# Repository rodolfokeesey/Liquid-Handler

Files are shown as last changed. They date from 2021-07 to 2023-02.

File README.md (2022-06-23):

# Liquid-Handler

Welcome to the github page for the SideKick liquid handler!

The Sidekick is a desktop liquid dispensing robot, compatible with standard SBS microplates designed for accessible laboratory automation. The Sidekick features an armature-based motion system and a fully 3D printed chassis to reduce overall mechanical complexity and build time, and accommodate user modification. Liquid dispensing is achieved by using four calibration-free solenoid driven positive displacement  pumps that deliver 10 microliter increments. Control is provided over a USB serial interface using a simple vocabulary of commands, implemented in the form of a short Micro Python program. At a total price of $710, the Sidekick offers laboratories an easy to build, easily maintained, open-source liquid handling system for both research and pedagogical introductions to lab automation. 

A complete description of the project and build instructions is available in R. Keesey, R, LeSeur, J. Schrier, “Sidekick: A Low-Cost Open-Source 3D Printed Liquid Dispensing Robot” _Hardware X_ 12, E00319 (2022) [doi:10.1016/j.ohx.2022.e00319](https://doi.org/doi:10.1016/j.ohx.2022.e00319)  

You can also see a video of it in action online: https://www.youtube.com/watch?v=fTURNI88WFQ

But if you don't want to read the paper, and just want to get started with building, take a look at the assembly guide located in the "Supporting Documentation" folder. This currently covers the mechanical assembly, the wiring, and getting started with the Sidekick's software.

Copyright Rodolfo Keesey 2022.                                                    
                                                                             
This source describes Open Hardware and is licensed under the CERN-OHL-S v2. 
                                                                             
You may redistribute and modify this source and make products using it under 
the terms of the CERN-OHL-S v2 (https://ohwr.org/cern_ohl_s_v2.txt).         
                                                                             
This source is distributed WITHOUT ANY EXPRESS OR IMPLIED WARRANTY,          
INCLUDING OF MERCHANTABILITY, SATISFACTORY QUALITY AND FITNESS FOR A         
PARTICULAR PURPOSE. Please see the CERN-OHL-S v2 for applicable conditions.  
                                                                             
Source location: https://github.com/rodolfokeesey/Liquid-Handler                                        
                                                                             
As per CERN-OHL-S v2 section 4, should You produce hardware based on this    
source, You must where practicable maintain the Source Location visible      
on the external case of the Gizmo or other products you make using this      
source.

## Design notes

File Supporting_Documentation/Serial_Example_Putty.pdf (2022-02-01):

Step 1: Determining the COM port

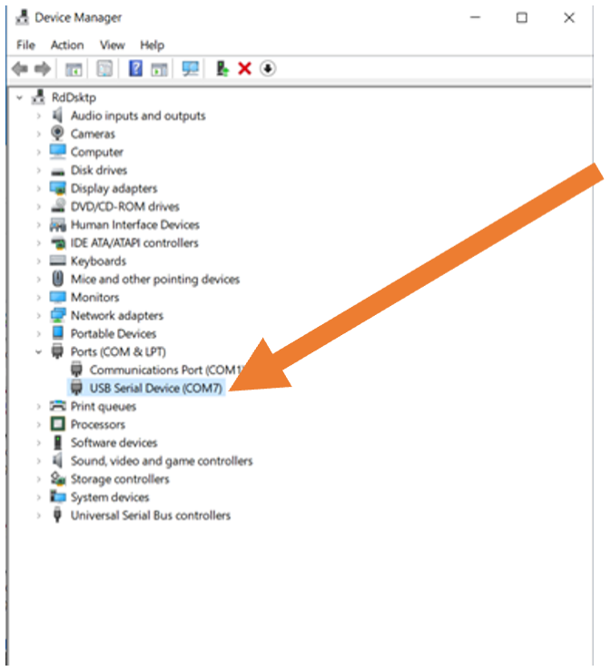
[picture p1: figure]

Figure 1: Checking the Sidekick COM port in Windows 10 device manager

The Sidekick reads commands from the USB serial port, allowing any application or programming environment that supports serial I/O to communicate with it. We recommend using Thonny or a serial terminal program such as Putty (on Windows), or the built-in “screen” command line program (on Mac/Linux).

To use Putty, first find the Sidekick’s com port, and baud rate. These are easy to find in Windows with the device manager. Go to Device Manager -> Ports -> USB Serial Device (Fig. 1). Our Sidekick is located at COM7 (on Windows) or /dev/tty.usbmodem0000000000001 (on Mac/Linux). If you are unsure which port your Sidekick occupies, unplug it, and see which port disappears.

Step 2: Determining Baud

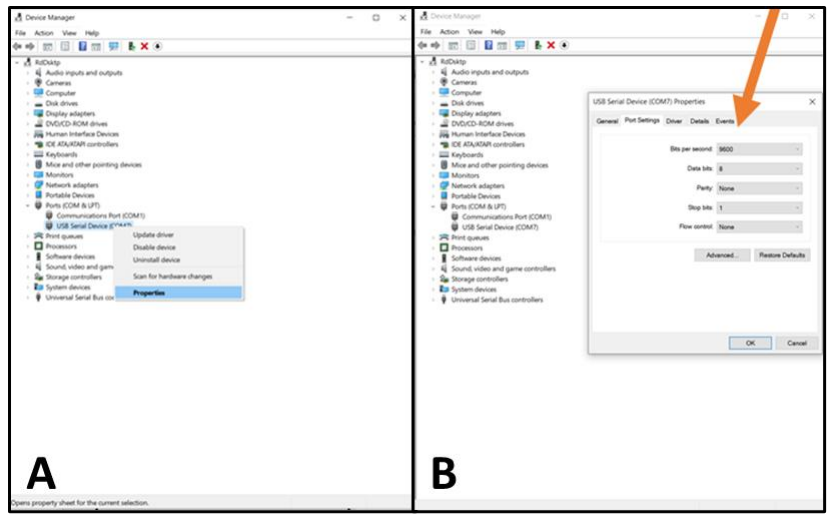
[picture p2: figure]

Figure 2A: Device Manager drop down. | B: Sidekick Baud in Device Manager Properties

Right click on the USB Serial Device. Click “Properties” in the drop down (Fig. 2a). Then click port settings. Make a note of the indicated bits per second, or baud (Fig. 2b).

Step 3: Connecting Via Putty

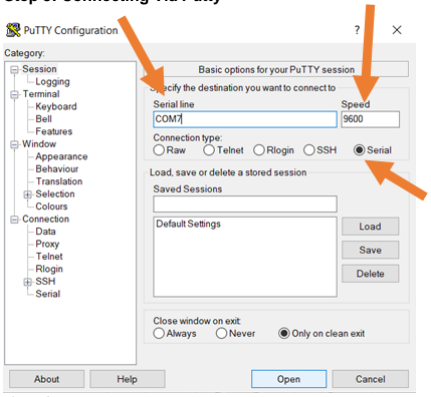
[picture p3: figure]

Figure 3: Putty startup UI

Now that we have the com port and the baud, we can use Putty to open a serial connection.
Download and install Putty: https://www.putty.org/
Once Putty is installed, open the application. Press the “Serial” option, and then input the correct com port we found in Step 1 under “Serial line”. Then input the baud rate we found in Step 3 under “Speed” (Fig. 3).
Step 4: Opening Putty and Sending Commands

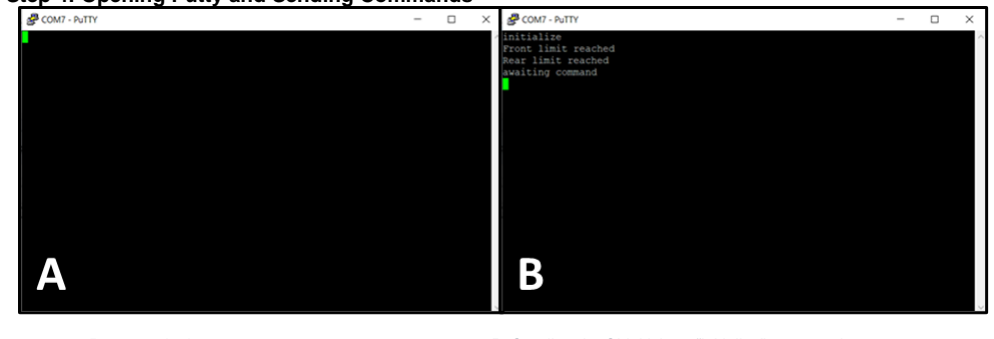
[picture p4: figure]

Figure 4a: Putty terminal | B: Sending the Sidekick an “initialize” command

After pressing open, the command line screen will appear (Fig. 4a). Type “initialize” (followed by return) to test communication with the Sidekick (Fig. 4b). The Sidekick should home against the limit switches, and output to the terminal. The Sidekick is now online and prepared to receive commands.

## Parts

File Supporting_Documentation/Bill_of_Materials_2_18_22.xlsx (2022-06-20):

Item | Items needed | Items per Unit Purchased | Units Purchased | Unit Cost | Bulk Cost (100 units) | Total Cost | Cost per Item needed | Link | Alternate Link | Comments
Overture PETG 1KG | 1 | 1 | 1 | 22.99 | NA | 22.99 | 22.99 | https://www.amazon.com/OVERTURE-Filament-Consumables-Dimensional-Accuracy/dp/B07PGYHYV8?s=industrial
3x10x4mm Ball bearings | 3 | 10 | 1 | 9.99 | NA | 9.99 | 2.997 | https://www.amazon.com/uxcell-Groove-Bearing-Double-Bearings/dp/B07FW257LJ
M2/3/4 Hardware (Button Head) | 1 | 1 | 1 | 23.99 | NA | 23.99 | 23.99 | https://www.amazon.com/Stainless-Assortment-820PCS-VIGRUE-Washers/dp/B098KXZNY6?s=industrial
M3 Hardware | 1 | 1 | 1 | 11.99 | NA | 11.99 | 11.99 | https://www.amazon.com/Stainless-Assortment-Precise-Beautiful-Printed/dp/B0714FLXND
PTFE Tubing 1/16" OD | 1 | 5 | 1 | 40.31 | NA | 40.31 | 8.062 | https://www.amazon.com/Cole-Parmer-PTFE-Tubing-32-Pack/dp/B00PQZUD3I
PTFE Tubing 1/8" OD | 1 | 5 | 1 | 59.35 | NA | 59.35 | 11.87 | https://www.amazon.com/Cole-Parmer-PTFE-Tubing-16-pack/dp/B00T97OZD8
12 Volt PSU | 1 | 1 | 1 | 12.99 | NA | 12.99 | 12.99 | https://www.amazon.com/LEDMO-Power-Supply-Transformers-Adapter/dp/B01461MOGQ
Power Barrel | 1 | 1 | 1 | 1.25 | NA | 1.25 | 1.25 | https://www.sparkfun.com/products/119
Breakaway Male Header Pins (40 Count) | 5 | 1 | 5 | 1.5 | 0.23 | 7.5 | 7.5 | https://www.sparkfun.com/products/116
Buttons | 1 | 1 | 4 | 0.25 | 0.2 | 1 | 0.25 | https://www.digikey.com/en/products/detail/apem-inc/MJTP1230E/1795785
Jumper Cables | 22 | 120 | 1 | 7.98 | NA | 7.98 | 1.463 | https://www.amazon.com/gp/product/B07GCY6CH7/ref=ppx_yo_dt_b_asin_title_o04_s00?ie=UTF8&th=1
Limit Switch | 2 | 2 | 1 | 2.95 | NA | 2.95 | 2.95 | https://www.sparkfun.com/products/13014
The Lee Company Fixed Volume 10μL Dispense Pumps (LPMA1250110L) | 4 | 1 | 4 | 135 | 120 | 540 | 540 | https://www.theleeco.com/products/electro-fluidic-systems/dispense-pumps/fixed-volume-dispense-pumps/lpm-series-pumps/
PCB | 1 | 5 | 1 | 3.1 | NA | 3.1 | 0.62 | https://jlcpcb.com/
Micrcontroller (Raspberry Pi Pico) | 1 | 1 | 1 | 4 | NA | 4 | 4 | https://www.digikey.com/en/products/detail/raspberry-pi-(trading)-ltd/SC0915/13684020
Darlington Array | 1 | 10 | 1 | 7.99 | NA | 7.99 | 0.799 | https://www.amazon.com/Bridgold-ULN2803APG-ULN2803-Darlington-High-Voltage/dp/B07W5WRG56
Stepper Motor Driver | 2 | 5 | 1 | 28.99 | NA | 28.99 | 11.596 | https://www.amazon.com/FYSETC-Stepstick-Heatsink-Ramps1-4-Board-5Pcs/dp/B08M9J8SB7
0.9deg Nema 17 Stepper Motor Bipolar | 2 | 1 | 2 | 22.99 | NA | 45.98 | 45.98 | https://www.amazon.com/Stepper-Pancake-LDO-42STH25-1404MAC-Printer-Extruder/dp/B089G8HZ51 | https://www.aliexpress.com/item/2251832831935819.html?pdp_ext_f=%7B%22sku_id%22%3A%2267236436630%22%7D | The amazon provider often seems to be out of stock.
Prices and Links Valid as of 2/18/22 |  |  |  |  | Quantity 1, 4 Pump Configuration Cost: | 832.35
 |  |  |  |  | 4 Pump Configuration, Unit Cost | 711.297

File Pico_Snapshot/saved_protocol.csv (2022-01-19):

Pump | Location | Amount
p1 | a1 | 150
p1 | a2 | 150
p1 | a3 | 150
p1 | a4 | 150
p1 | a5 | 150
p2 | a6 | 150
p2 | a7 | 150
p2 | a8 | 150
p2 | a9 | 150
p2 | a10 | 150
p2 | a11 | 150
p2 | a12 | 150
p1 | b1 | 150
p1 | b2 | 150
p1 | b3 | 150
p1 | b4 | 150
p1 | b5 | 150
p3 | b6 | 150
p3 | b7 | 150
p3 | b8 | 150
p3 | b9 | 150
p3 | b10 | 150
p3 | b11 | 150
p3 | b12 | 150
p1 | c1 | 150
p1 | c2 | 150
p1 | c3 | 150
p1 | c4 | 150
p1 | c5 | 150
p2 | c6 | 150
p2 | c7 | 150
p2 | c8 | 150
p2 | c9 | 150
p2 | c10 | 150
p2 | c11 | 150
p2 | c12 | 150
p1 | d1 | 150
p1 | d2 | 150
p1 | d3 | 150
p1 | d4 | 150
p1 | d5 | 150
p3 | d6 | 150
p3 | d7 | 150
p3 | d8 | 150
p3 | d9 | 150
p3 | d10 | 150
p3 | d11 | 150
p3 | d12 | 150
p2 | e1 | 150
p2 | e2 | 150
p2 | e3 | 150
p2 | e4 | 150
p2 | e5 | 150
p2 | e6 | 150
p2 | e7 | 150
p2 | e8 | 150
p2 | e9 | 150
p2 | e10 | 150
p2 | e11 | 150
p2 | e12 | 150
p3 | f1 | 150
p3 | f2 | 150
p3 | f3 | 150
p3 | f4 | 150
p3 | f5 | 150
p3 | f6 | 150
p3 | f7 | 150
p3 | f8 | 150
p3 | f9 | 150
p3 | f10 | 150
p3 | f11 | 150
p3 | f12 | 150
p2 | g1 | 150
p2 | g2 | 150
p2 | g3 | 150
p2 | g4 | 150
p2 | g5 | 150
p2 | g6 | 150
p2 | g7 | 150
p2 | g8 | 150
p2 | g9 | 150
p2 | g10 | 150
p2 | g11 | 150
p2 | g12 | 150
p3 | h1 | 150
p3 | h2 | 150
p3 | h3 | 150
p3 | h4 | 150
p3 | h5 | 150
p3 | h6 | 150
p3 | h7 | 150
p3 | h8 | 150
p3 | h9 | 150
p3 | h10 | 150
p3 | h11 | 150
p3 | h12 | 150

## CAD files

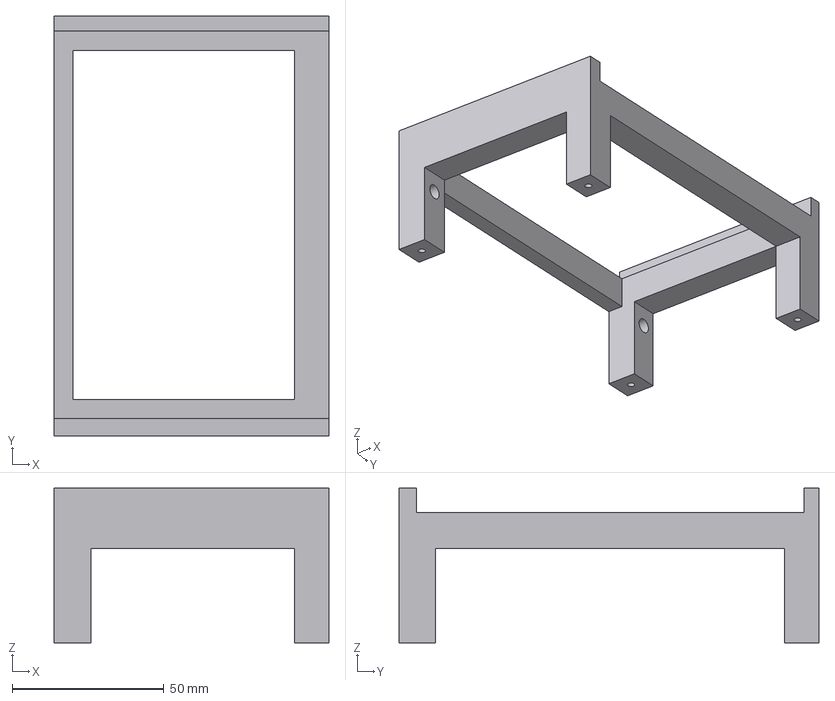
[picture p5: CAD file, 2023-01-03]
3D_Assets/96WellTrayHolder_Reservoir/96 Well Holder.step
90.6 x 138.5 x 51.1 mm

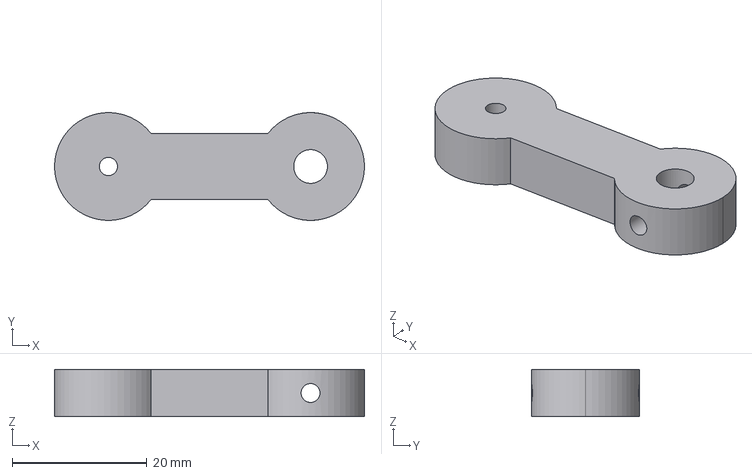
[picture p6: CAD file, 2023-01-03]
3D_Assets/Armature/Arm Two.step
46.0 x 16.0 x 7.00 mm

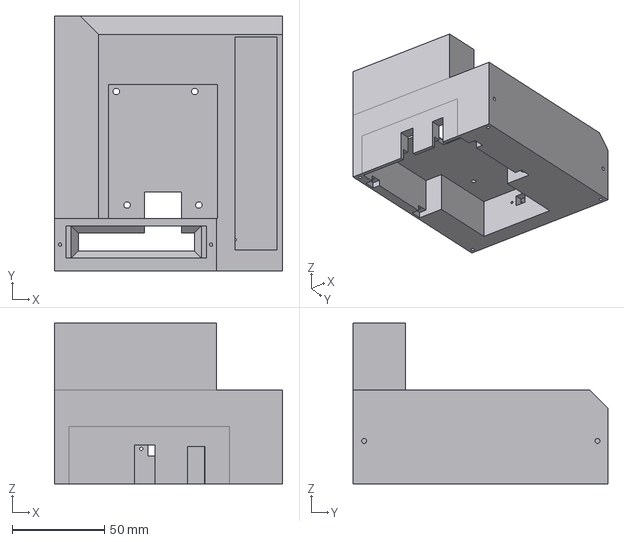
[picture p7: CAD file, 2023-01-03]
3D_Assets/MainBody/Base.step
124.0 x 138.5 x 87.2 mm

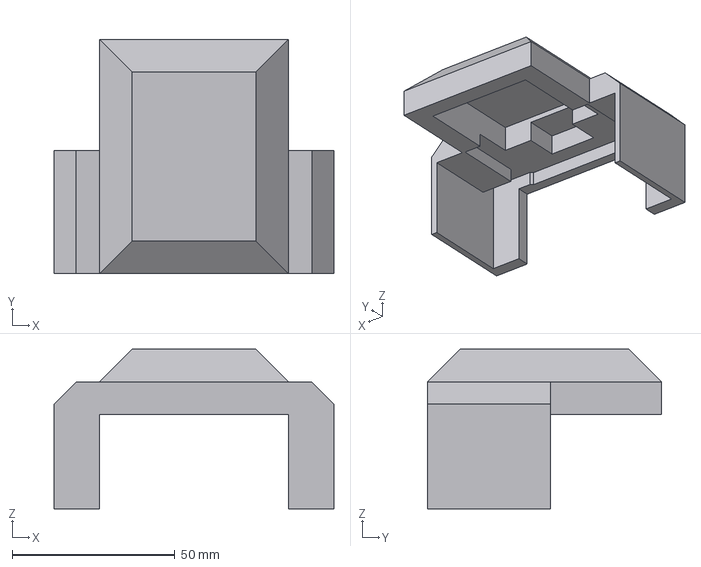
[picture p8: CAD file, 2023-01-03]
3D_Assets/MotorMounts/Motor Cap New (Unvalidated).step
86.0 x 72.0 x 49.0 mm

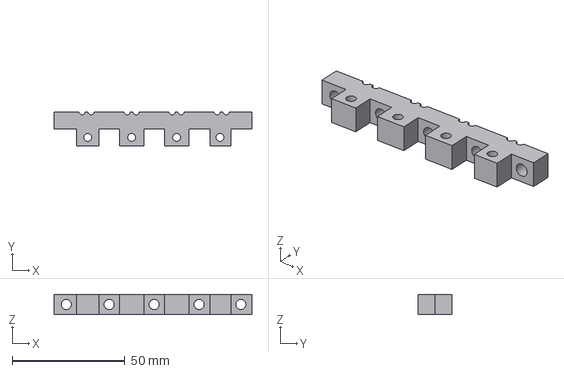
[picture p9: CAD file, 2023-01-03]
3D_Assets/Pumps/Front Adapter Clamp.step
88.0 x 15.3 x 9.00 mm

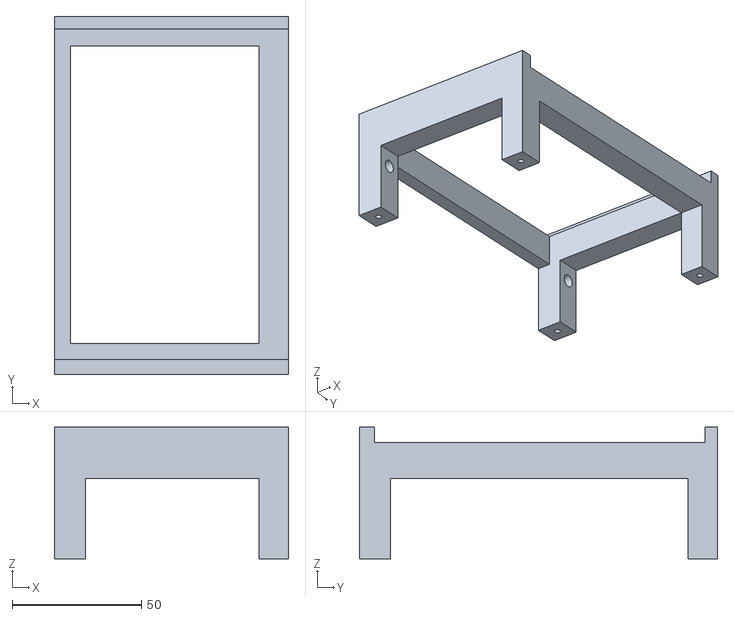
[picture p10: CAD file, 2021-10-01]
3D_Assets/96WellTrayHolder_Reservoir/96 Well Plate Holder.stl
90.5 x 138.5 x 51.0

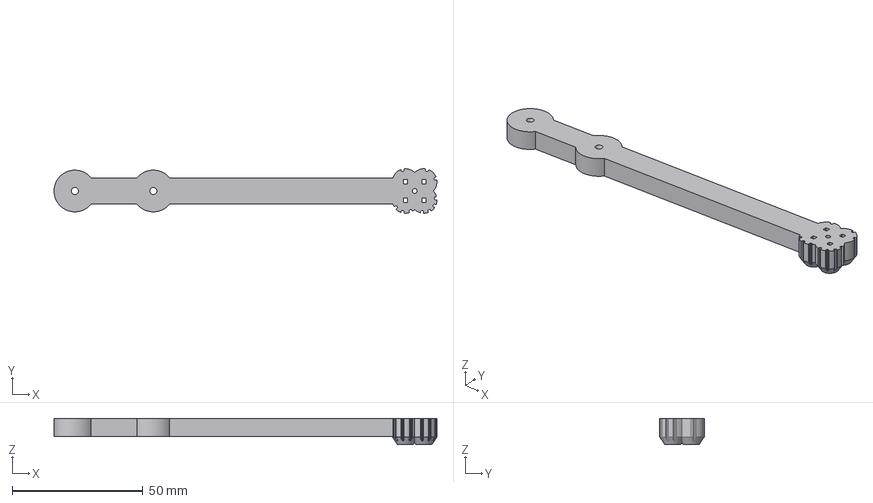
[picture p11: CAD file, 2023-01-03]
3D_Assets/Armature/Arm Four.step
146.5 x 17.1 x 10.0 mm

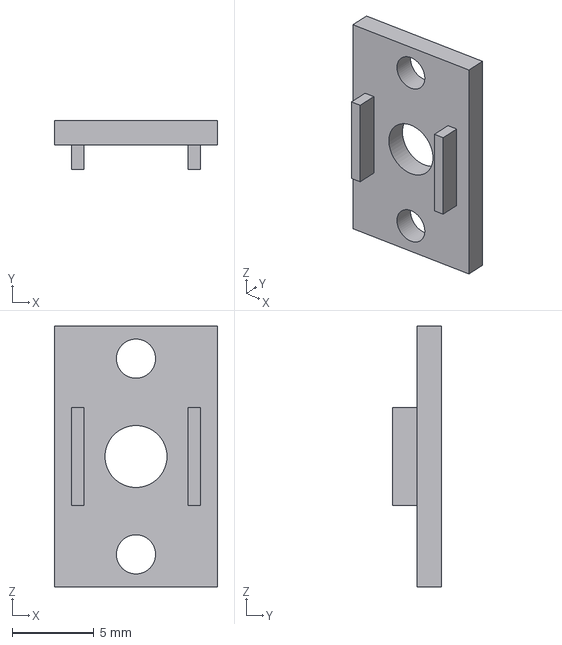
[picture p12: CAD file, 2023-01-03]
3D_Assets/MainBody/Button Housing Front.step
10.0 x 3.00 x 16.0 mm

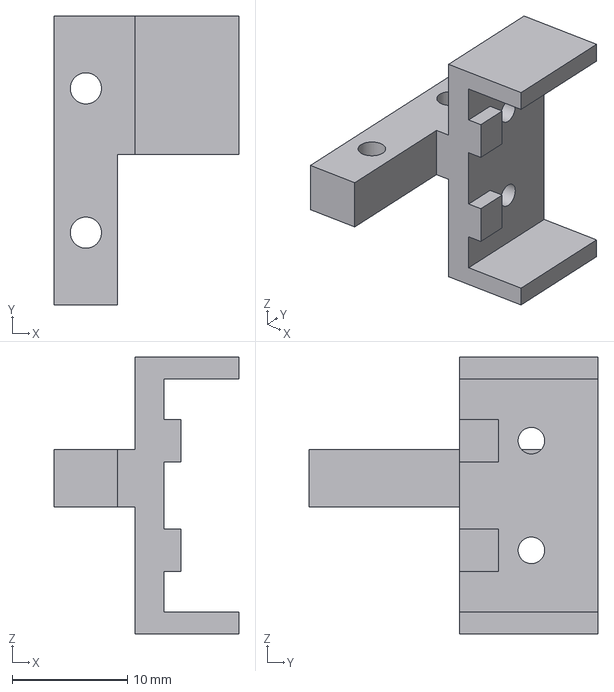
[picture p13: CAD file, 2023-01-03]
3D_Assets/MotorMounts/Front Switch Mount.step
16.0 x 25.0 x 24.0 mm

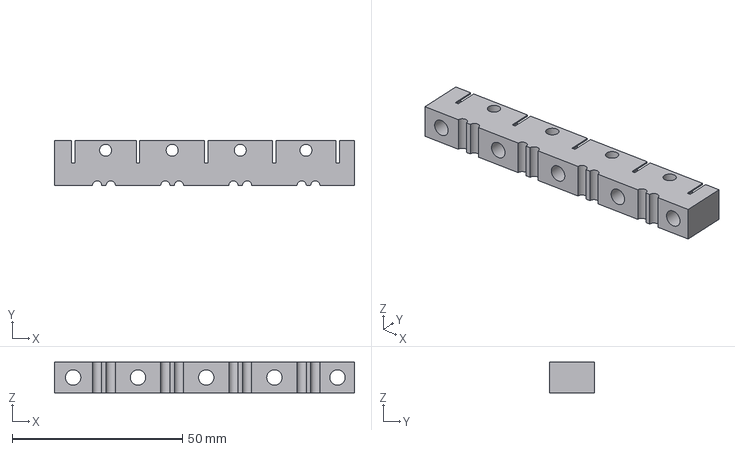
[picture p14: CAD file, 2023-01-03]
3D_Assets/Pumps/Rear Adapter Clamp.step
88.0 x 13.2 x 9.00 mm

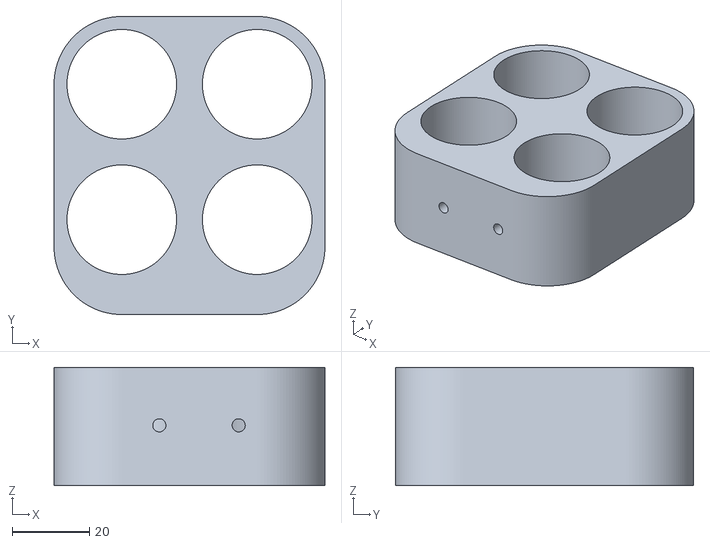
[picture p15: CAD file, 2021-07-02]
3D_Assets/96WellTrayHolder_Reservoir/50ml Tube Holder.stl
70.0 x 77.0 x 30.5

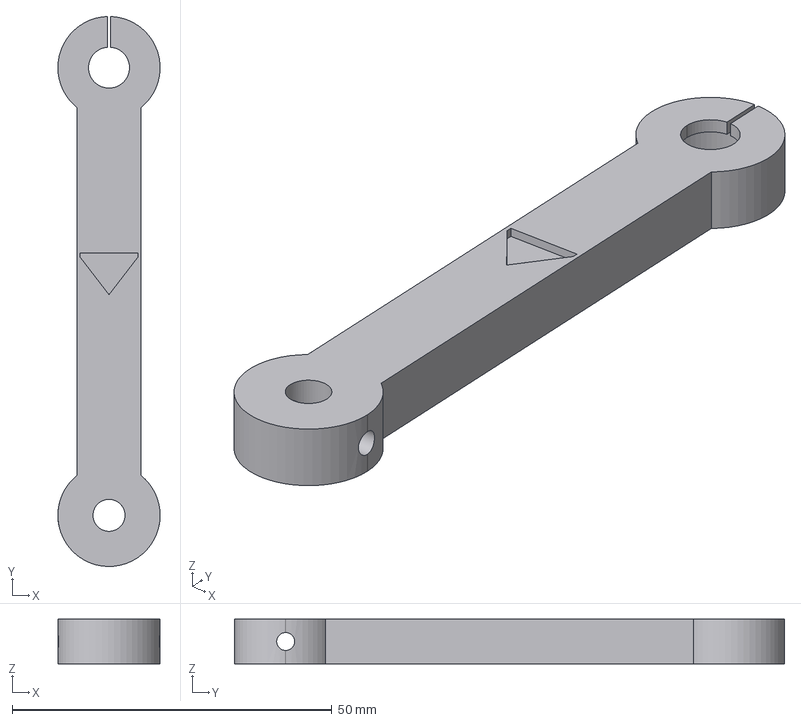
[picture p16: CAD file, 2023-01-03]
3D_Assets/Armature/Arm One.step
16.0 x 86.0 x 7.00 mm

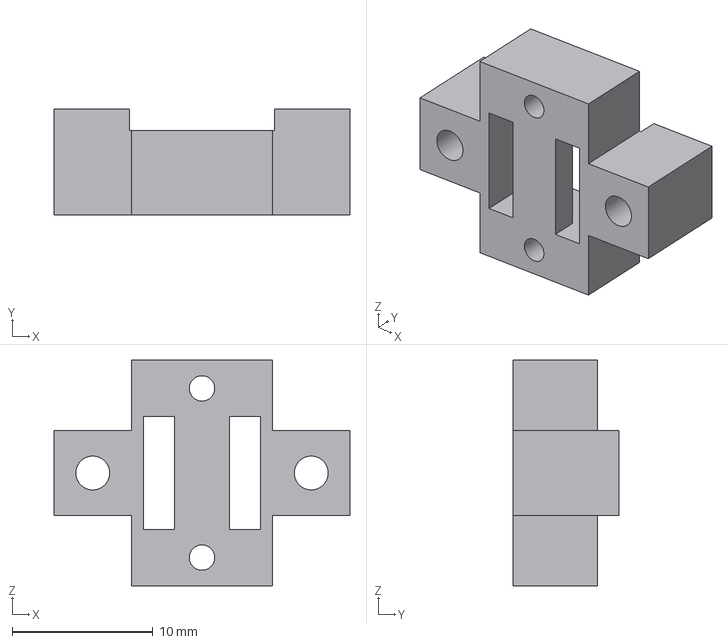
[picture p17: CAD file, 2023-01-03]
3D_Assets/MainBody/Button Housing.step
21.0 x 7.50 x 16.0 mm

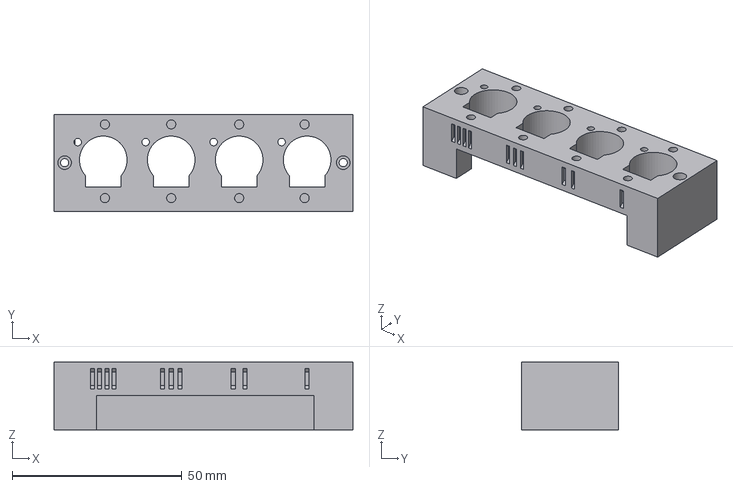
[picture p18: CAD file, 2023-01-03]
3D_Assets/Pumps/Pump Mount.step
88.0 x 28.5 x 20.0 mm

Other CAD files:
3D_Assets/MotorMounts/Rear Switch Mount.step
3D_Assets/Armature/Arm Three.step
3D_Assets/MainBody/Foot.step
3D_Assets/MotorMounts/Lower Motor Mount.step
3D_Assets/96WellTrayHolder_Reservoir/96 Well Holder.f3d
3D_Assets/Armature/Arm Four.f3d
3D_Assets/Armature/Arm Four.stl
3D_Assets/Armature/Arm One.f3d
3D_Assets/Armature/Arm One.stl
3D_Assets/Armature/Arm Three.f3d
3D_Assets/Armature/Arm Three.stl
3D_Assets/Armature/Arm Two.f3d
3D_Assets/Armature/Arm Two.stl
3D_Assets/MainBody/Base.f3d
3D_Assets/MainBody/Base.stl
3D_Assets/MainBody/Button Housing Front.f3d
3D_Assets/MainBody/Button Housing Front.stl
3D_Assets/MainBody/Button Housing.f3d
3D_Assets/MainBody/Button Housing.stl
3D_Assets/MainBody/Foot.f3d
3D_Assets/MainBody/Foot.stl
3D_Assets/MainBody/PCB Tray.f3d
3D_Assets/MainBody/PCB Tray.step
3D_Assets/MainBody/PCB Tray.stl
3D_Assets/MotorMounts/Front Switch Mount.f3d
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

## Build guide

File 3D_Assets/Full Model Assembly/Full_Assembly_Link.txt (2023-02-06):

The full model of the Sidekick is too large to host on GitHub. 

You can download it here (.STEP):

https://drive.google.com/file/d/1ixu_sJcHN8C959OuZ0lleuiCjruZTeNM/view?usp=sharing

Or here (.f360):

https://drive.google.com/file/d/1-_fRdbV1oF3euVx34Ysh9thHAF1UIZZc/view?usp=sharing

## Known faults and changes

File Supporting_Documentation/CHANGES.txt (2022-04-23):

In accordance with CERN-OHL-S v2, anyone modifying the design should provide brief information about the modifications,
including the date they were made, in this text document. 

Information about this design and modification should be added to this text file, but never removed.

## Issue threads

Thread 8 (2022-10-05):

### ISSUE TITLE
[HARDWARE]: Where can i buy the LPM pump? The only way i can found is texting with company supporter. Are there anyway to buy its?

### ISSUE THREAD

**Issue by Binh2542** [rodolfokeesey/Liquid-Handler#8]
[HARDWARE]: Where can i buy the LPM pump? The only way i can found is texting with company supporter. Are there anyway to buy its?

**Comment by jschrier** [comment]
Correct.  You must contact [Lee Company](https://www.theleeco.com/) to purchase the LMP pumps.  They are the only vendor.

**Comment by jschrier** [comment]
Possible alternatives (which we haven't tried yet): Takasago Fluidics  https://www.takasago-fluidics.com/products/mcp?variant=34641036279974   These are roughly $200 ea, so it does not reduce costs.

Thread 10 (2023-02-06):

### ISSUE TITLE
Fusion360 files for the design

### ISSUE THREAD

**Issue by jschrier** [rodolfokeesey/Liquid-Handler#10]
@rodolfokeesey — I had thought that the `3D_Assets` contained the Fusion360 file, but this does not appear to be present.  Can you upload this?  We have an engineering student coming on, who is going to work on modifying the design.

**Comment by rodolfokeesey** [comment]
Can do! Out traveling, but I will try to get STEP files in today, and F360 files once I get to a machine with access to it.

**Comment by rodolfokeesey** [comment]
Ok! f360 files and STEP files are included for all the 3D models. A google drive link was also added containing .STEP and .f360 files of the fully assembled Sidekick.

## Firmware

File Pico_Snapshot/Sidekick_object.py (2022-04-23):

from machine import Pin
import time
import kinematicsfunctions as kf
import plategen

class Sidekick:
    
    def __init__(self,L1,L2,L3,Ln,Origin,Home,Effector_Location):
        
        # Dimensional Attributes (in cm)
        
        self.L1 = L1
        self.L2 = L2
        self.L3 = L3
        self.Ln = Ln
        
        # Locational Attributes, home is subject to change, right now it is over well a12
        self.home = [90,178]  # there is a `Home` parameter not used in init
        self.origin = Origin
        self.current = Effector_Location #Angular location of stepper
        self.purge = self.loadpurge() #[45.7808, 89.6624]
        self.stepsize = .1125 # 8 microsteps at 0.9 degree motor, 
        self.stepdelay = .0010
        

        # Center Well Lookup Map, saved as platemap1.txt
        
        self.plateinfo = self.loadplate()
        self.alltheta1 = self.plateinfo[0]
        self.alltheta2 = self.plateinfo[1]
        self.wellids = self.plateinfo[2]
        
        
        ########## Hardware attributes, Motor 1 is the top motor, Motor 2 is the bottom motor
        
        ##### Stepper Motor 2 Setup, Bottom Motor
        
        # 1.8 degree steppers, order from top: red,blue,green,black
        
        # Step Pin
        self.motor2 = Pin(10, Pin.OUT)
        self.motor2.value(0)

        # Direction Pin

        self.motor2_d = Pin(9, Pin.OUT)
        self.motor2_d.value(0)

        # Mode Pins

        self.motor2_m0 = Pin(15, Pin.OUT)
        self.motor2_m1 = Pin(14, Pin.OUT)

        # Sleep Pin

        self.motor2_sleep = Pin(16, Pin.OUT)
        self.motor2_sleep.value(0)

        # Setting Mode to 1/8 step, so 0.45 degrees per step on a 1.8 degree stepper

        self.motor2_m0.value(0)
        self.motor2_m1.value(0)
        
        
        ##### Stepper Motor 1 Setup, Top Motor
        # 1.8 degree steppers, order from top: blue,red,green,black

        # Step Pin
        self.motor1 = Pin(1, Pin.OUT)
        self.motor1.value(0)

        # Direction Pin

        self.motor1_d = Pin(0, Pin.OUT)
        self.motor1_d.value(0)

        # Mode Pins

        self.motor1_m0 = Pin(6, Pin.OUT)

        self.motor1_m1 = Pin(5, Pin.OUT)

        # Sleep Pin

        self.motor1_sleep = Pin(7, Pin.OUT)
        self.motor1_sleep.value(0)

        # Setting Mode to 1/8 step, so 0.45 degrees per step

        self.motor1_m0.value(0)
        self.motor1_m1.value(0)
        
        ##### Limit Switch Setup #####
        
        # Front Limit Switch, when activated, lsfront.value = false
        
        self.lsfront = Pin(18, Pin.IN, Pin.PULL_UP)
     
        # Rear Limit Switch, when activated, lsrear.value = false
        
        self.lsrear = Pin(19, Pin.IN, Pin.PULL_UP)
        
        ##### Purge Button #####
        
        self.purgebutton = Pin(20, Pin.IN, Pin.PULL_UP)

        
        ##### Pump Setup #####
        
        # Pump 1
        self.pump1 = Pin(27, Pin.OUT)
        self.pump1.value(0)
        
        # Pump 2
        self.pump2 = Pin(26, Pin.OUT)
        self.pump2.value(0)
        
        # Pump 3
        self.pump3 = Pin(22, Pin.OUT)
        self.pump3.value(0)
        
        # Pump 4
        self.pump4 = Pin(21, Pin.OUT)
        self.pump4.value(0)
    
    # Sidekick Functions
    
    # Plate loading function
    
    @staticmethod
    def loadplate():
        """Take the save text file of well coordinates and read it into memory."""
        
        platefile = open("platemap1.txt","r")
        emptyplate = platefile.read().replace('\r','')
        emptyplate = emptyplate.split("\n")
        platelength = int((len(emptyplate) - 4)/3)
        sectionlength = int((len(emptyplate) - 1)/3)
   
        theta_one = [float(coords) for coords in emptyplate[1:sectionlength] ]
        theta_two = [float(coords) for coords in emptyplate[sectionlength+1:sectionlength*2] ]
        well_ids = emptyplate[(sectionlength*2)+1:len(emptyplate)-1]
        platefile.close()
        return[theta_one,theta_two,well_ids]
    
    # Purge location loading
    
    @staticmethod
    def loadpurge():
        """Take the save text file of purge coordinates and read it into memory."""
        
        purgefile = open("purge1.txt","r")
        purgeloc = purgefile.read()
        purgeloc = purgeloc.split("\n")
        purgeloc = [float(coords) for coords in purgeloc]
        purgefile.close()
        return purgeloc
        
    
    # One step command for the steppers.
    
    def motor1_onestep(self,direction):
        """Command stepper motor 1 to move one step, False is CCW, True is CW"""
        
        self.motor1_d.value(direction) # False is CCW, True is CW
        self.motor1.value(0)
        time.sleep(self.stepdelay)
        self.motor1.value(1)
        time.sleep(self.stepdelay)
        
    def motor2_onestep(self,direction):
        """Command stepper motor 1 to move one step, False is CCW, True is CW"""
        
        self.motor2_d.value(direction) # False is CCW, True is CW
        self.motor2.value(0)
        time.sleep(self.stepdelay)
        self.motor2.value(1)
        time.sleep(self.stepdelay)
    
    # Basic movement function. Moves the steppers to a new angular position, then updates current angular position.

    
    def advangleboth(self,newangle1,newangle2):
        """Move the steppers to a new angular position, update current angular position."""
    
        steps_one = round(abs(newangle1-self.current[0])/self.stepsize)
        final_one = self.current[0] + (round((newangle1-self.current[0])/self.stepsize))*self.stepsize
        steps_two = round(abs(newangle2-self.current[1])/self.stepsize)
        final_two = self.current[1] + (round((newangle2-self.current[1])/self.stepsize))*self.stepsize
        
        if steps_one <= steps_two:
            for x in range(steps_one):
                if self.current[0] <= newangle1:
                    self.motor1_onestep(0) #style=stepper.INTERLEAVE
                    time.sleep(self.stepdelay)
                else:
                    self.motor1_onestep(1) #style=stepper.INTERLEAVE
                    time.sleep(self.stepdelay)
                if self.current[1] <= newangle2:
                    self.motor2_onestep(0) #style=stepper.INTERLEAVE
                    time.sleep(self.stepdelay)
                else:
                    self.motor2_onestep(1) #style=stepper.INTERLEAVE
                    time.sleep(self.stepdelay)
            for x in range(steps_two-steps_one):
                if self.current[1] <= newangle2:
                    self.motor2_onestep(0) #style=stepper.INTERLEAVE
                    time.sleep(self.stepdelay*2)
                else:
                    self.motor2_onestep(1) #style=stepper.INTERLEAVE
                    time.sleep(self.stepdelay*2)
            self.current[0] = final_one
            self.current[1] = final_two
        
        if steps_two < steps_one:
            for x in range(steps_two):
                if self.current[0] <= newangle1:
                    self.motor1_onestep(0) #style=stepper.INTERLEAVE
                    time.sleep(self.stepdelay)
                else:
                    self.motor1_onestep(1) #style=stepper.INTERLEAVE
                    time.sleep(self.stepdelay)
                if self.current[1] <= newangle2:
                    self.motor2_onestep(0) #style=stepper.INTERLEAVE
                    time.sleep(self.stepdelay)
                else:
                    self.motor2_onestep(1) #style=stepper.INTERLEAVE
                    time.sleep(self.stepdelay)
            for x in range(steps_one-steps_two):
                if self.current[0] <= newangle1:
                    self.motor1_onestep(0) #style=stepper.INTERLEAVE
                    time.sleep(self.stepdelay*2)
                else:
                    self.motor1_onestep(1) #style=stepper.INTERLEAVE
                    time.sleep(self.stepdelay*2)
            
            self.current[0] = final_one
            self.current[1] = final_two
    
    # Plate Cycling, allows the user to cycle through the plating process. Good for spotting misalligned plates.
    
    def platecycle(self):
        """Allow the user to cycle through the plating process."""
        
        platecycle = input("Would you like to cycle through the plating process? 'yes' or 'no'  ")

        if platecycle == "yes":
            for well in self.wellids:
                thetas = kf.angle_lookup(well,self.wellids,self.alltheta1,self.alltheta2)
                self.advangleboth(thetas[0], thetas[1])
                print(well, "| ideal thetas:", thetas, "actual thetas:", self.current)
                time.sleep(.4)
                #self.pumpcycle()

            # Return to Starting Position
            self.advangleboth(self.home[0], self.home[1])
    
    # Pump Cycling, places each pump over the centerpoint, mostly for troubleshooting/reliability testing
    
    def pumpcycle(self):
        """Places each pump over the armature centerpoint."""
        
        print(self.current)
        
        center = kf.forward_kinematics(self.L1,self.L2,self.L3,self.current[0],self.current[1])
        centerthetas = [self.current[0],self.current[1]]
        
        print(centerthetas)
        
        #loop over the different pump positions
        for position in ["N1","N2", "N3","N4"]:
            thetas = kf.inverse_kinematics_multi(self.L1,self.L2,self.L3,self.Ln,position,center,self.origin)
            self.advangleboth(thetas[0], thetas[1])
            time.sleep(.8)
        
        print(self.current)
        self.advangleboth(centerthetas[0], centerthetas[1])
        print(self.current)
    

    ##%% PUMP MOVEMENT METHODS
    
    # Simple move to well function. Moves indicated effector to target well
    
    def movetoXY(self, effector, x, y):
        """Move indicated effector to target well as specified by a cartesian X,Y pair"""
        if effector == "center":
            #Calculates the angular position from given x,y
            thetas = kf.inverse_kinematics(self.L1,self.L2,self.L3,self.origin,[x,y])
            try:
                self.advangleboth(thetas[0], thetas[1])
            except:
                print("Cannot move to position")
        elif effector in {"p1", "p2", "p3", "p4"}:
            pump_label = effector.replace("p","N")
            thetas = kf.inverse_kinematics_multi(self.L1,self.L2,self.L3,self.Ln,pump_label,[x,y],self.origin)
            try:
                self.advangleboth(thetas[0], thetas[1])
            except:
                print("Cannot move to position")
        else:
            print("Indicated pump not recognized")
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

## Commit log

2021-04-16 Add files via upload
    Matlab Kinematics. This code was used to generate the 96 well plate to servo angles table.
2021-04-16 Add files via upload
    Kinematic Functions to call for determining servo angle from well ID. There's also a function for determining servo location from an (x,y) coordinate from the origin in cm.
2021-07-02 Add files via upload
    Python code needed to run the current Sidekick. Import the sidekick object into a new script. Poke around the sidekick_object_v2 file to see the functionality. I'll post some better documentation as 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
2021-07-02 Add files via upload
    A diagram of the prototype sidekick, as well as a link to a demo
2021-10-01 10_1_21, Latest Prototype Upload
    Uploaded PCB Schematics, latest 3D assets, current working code, and build guide
    [50ml_tubeholder.stl, Armature_Leg Four V6.stl, Armature_Leg One V6.stl, Armature_Leg Three V6 Multichannel (1).stl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]
2021-10-06 10_6_21 Update
    Finished off main loop and updated documentation
    [flag_demo_cheat.csv]
2021-10-25 Added Limit Switch Holders
    [50ml Tube Holder.stl, 50ml_tubeholder.stl, 96 Well Plate Holder.stl, Adapter Clamp Front 2.stl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]
2021-11-05 11_5_21 Readability updates
    Deleted duplicates, and removed spaces in folder titles.
    [50ml Tube Holder.stl, 96 Well Plate Holder.stl, Adapter Clamp Front 2.stl, Adapter Clamp Front 3.stl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]
2021-11-25 Updated Pump Adapters
    New Pump Adapters to test! Designed a monolithic pump adapter that tightens onto all pumps at once, and secures the tubing assembly to the pump mount. Did some testing at Haverford, and they worked w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
    [PumpAdapterV2.stl, PumpAdapterV2Backplate.stl, PumpAdapterV2_Mount.stl]
2021-11-29 Readme update/demo update
    Wrote a better readme, updated the demo sheet to work with the matlab parser.
    [flag_demo_cheat.csv]
2021-12-20 Add execute protocol
    Updates to re-add the "execute saved protocol" function
    [saved_protocol.csv]
2022-01-03 Updated 3D Assets
    Updated Armature and Pump 3D models
    [Adapter Clamp Front.stl, Adapter Clamp Rear.stl, Front Adapter Clamp.stl, Leg Four.stl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]
2022-01-04 Updated Snapshot
    Updated parser and saved protocol executer
    [saved_protocol.csv]
2022-01-04 Create Rear Adapter Clamp Larger.stl
    [Rear Adapter Clamp Larger.stl]
2022-01-10 Rename
    Legs to arms
    [Arm Four.stl, Arm One.stl, Arm Three.stl, Arm Two.stl]
2022-01-19 Code cleanup for readability
    [saved_protocol.csv]
2022-01-19 reviewing this code—is it used? a test?
    The function definition appeared invalid; I also made your for loop a bit more idiomatic by avoiding the iterator variable i
2022-02-01 Documentation updates
    Deleted old assembly instructions, added the putty serial connection example.
2022-03-02 cleaning
    Updated the old BOM, deleted old files, uploaded new assembly guide
    [Bill_of_Materials_10_6_21.xlsx, Bill_of_Materials_2_18_22.xlsx, Foot 5.stl, Foot 6.stl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]
2022-04-14 gcode units
    default for gcode is units of millimeters (screw support for inches). But kinematicsfunctions.py does everything in centimeters. So divide the gcode input by ten to make everything in centimeters. Ya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
2022-04-21 Updated Armature
    Updated armature with latest version
    [Arm Four.stl]
2022-04-23 3D Asset Update
    Updated Pump Mount and rear adapter clamp
    [Pump Mount.stl, Rear Adapter Clamp.stl]
2022-06-20 Update Bill_of_Materials_2_18_22.xlsx
    Added an alternate source for the stepper motors
    [Bill_of_Materials_2_18_22.xlsx]
2023-01-03 Added .step files
    Added the .step file for the 3D printed parts.
    [96 Well Holder.step, Arm Four.step, Arm One.step, Arm Three.step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]
2023-02-06 added f360 and full models
    Added the f360 format for all 3D assets. Created a new folder in 3D Assets containing a link to the full model in STEP form.
    [96 Well Holder.f3d, Arm Four.f3d, Arm One.f3d, Arm Three.f3d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]
